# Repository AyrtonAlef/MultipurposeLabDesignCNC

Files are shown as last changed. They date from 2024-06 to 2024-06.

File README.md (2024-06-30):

# Multipurpose Lab-design CNC

Development of a lab-design positioning system (CNC machine) with interchangeable head for different applications.

The positioning system allows precise control of the position and speed of the head along the stage plane. The distance between the head and the stage can be adjusted manually using a hand screw. Three head modules are available: (i) painting head, (ii) pencil head and (iii) cleaning head.

The painting head allows an airbrush to be attached and painting to be carried out in a controlled manner. The module was designed to work with a double-action airbrush. The air flow and paint intensity are controlled by a servo motor.

The pencil head allows a pencil or a pen to be attached. By activating a servo motor, the pencil/pencil is brought closer to the stage, allowing lines or curves to be drawn according to the movement of the positioning system. The pencil head can be used to perform pencil tests. The module ensures that the force, inclination and path traveled are kept constant throughout the test. According to the desired tilt angle, the can be fixed either 45° or 90° in relation to the stage.

The cleaning head includes a linear rod. The rod has a cylindrical end, allowing a cloth to be attached to assess the anti-stain properties of materials. The anti-stain property can be associated with the ease with which the material's surface can be cleaned. Thus, to characterize anti-stain property, the surface being evaluated can be contaminated and then cleaned. Images of the surface are captured before and after cleaning, allowing the surface's susceptibility to cleaning to be quantified. Images of the cloth used for cleaning can also be captured, in order to assess the ability to transfer contaminants to the cloth. To conduct the anti-stain test, it is necessary to ensure reproducibility in both contamination and cleaning steps. By using the cleaning head, it is possible to ensure that the cloth proximity to the contaminated surface, the cleaning path and the force are kept constant throughout the anti-stain test.

The electrical/electronic components, responsible for controlling the positioning system, are contained in a box that functions as a control panel, providing flexibility and safety in the use of the equipment. The control panel can be fully 3D printed, allowing the attachment of control boards (Arduino and CNC shield), command buttons (ON/OFF and emergency button), power source and cooling system.

The control of the positioning system (lab-design CNC) was performed using Grbl. To facilitate the insertion of commands by the user, the Universal G-Code Sender (UGS) was used. Grbl is free, open-source and high-performance software for controlling movement in machines, running directly on Arduino. UGS is a free gcode platform with several features for interfacing advanced CNC controls in different environments, such as Grbl.
In the root folder of the repository there is a text file (InstalationVer2.txt) with several instructions regarding the use of the positioning system. There you will find a description of the main elements used for control (stepper motor and servo motor), links to more information about the control programs used (Grbl, UGS and Arduino) and a step-by-step guide for initializing the device.

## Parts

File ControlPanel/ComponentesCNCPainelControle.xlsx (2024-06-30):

Qtdade | Descrição | Nome
1 | Placa inferior (impresso 3D - PLA) | CaixaBase
2 | Placa lateral (impresso 3D - PLA) | CaixaLateral
1 | Placa traseira (impresso 3D - PLA) | CaixaTraseira
1 | Placa frontal (impresso 3D - PLA) | CaixaFrente
1 | Placa superior (impresso 3D - PLA) | CaixaSuperior
1 | Chave Liga/Desliga | BotaoLigaDesliga
1 | Tomada painel plug conector macho 3 pinos | PlugueAlimentacaoFemea
1 | Arduino UNO R3 | arduino uno
1 | CNC Shield V3 (3D RepRap) | CNC shield.stp
1 | Fonte ATX colméia S60-12 -12 V, 5 A e 60 W Bivolt (Haiz) | Fonte
4 | Driver de motor de passo A4988 | -
1 | Botão de Emergência | BotaoEmergencia
1 | Cooler | Cooler

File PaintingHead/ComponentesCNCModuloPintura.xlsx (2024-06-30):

Qtdade | Descrição | Nome
1 | Suporte aerógrafo (impresso 3D - PLA) | MontagemSuporteAerografo
1 | Suporte traseira superior aerógrafo (impresso 3D - PLA) | SuporteCorpoAerografoVer3Part2
1 | Casco superior corpo aerógrafo (impresso 3D - PLA) | GatilhoSuporteSuperiorVer3
1 | Casco inferior corpo aeerógrafo (impresso 3D - PLA) | GatilhoSuporteinferior
1 | Caminho para acionamento (impresso 3D - PLA) | GatilhoSuporteCaminhoVer2
1 | Corrediça para acionamento (impresso 3D - PLA) | GatilhhoSuporteCorredicaVer2
1 | Capa para o gatilho (impresso 3D - PLA) | GatilhoBotao&HasteBotao_SuporteVer4
1 | Disco furato para servo motor (impresso 3D - PLA) | GatilhoServo
1 | Haste disco-corrediça (impresso 3D - PLA) | GatilhoHasteServo_SuporteVer4
1 | Micro servo motor Tower Pro 9gSg9 (Wtec) | SG90 - MicroServo 9g - Tower Pro.1
1 | Mini compressor de ar ON-10 (Onetools) | -
1 | Aerógrafo dupla ação copo fixo 0,3 mm (Onetools) | Aerografo
1 | Parafuso atarraxante Phillips 2,2x6,5 mm | -
4 | Parafuso Allen M3x25 mm | -
1 | Parafuso Allen M3x8 mm | -
1 | Parafuso Allen M3x10 mm | -
7 | Arruela lisa M3 | -
5 | Porca sextavada M3 | -

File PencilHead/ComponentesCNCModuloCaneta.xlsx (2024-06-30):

Qtdade | Descrição | Nome
1 | Suporte base caneta (impresso 3D - PLA) | MontagemSuporteCaneta
1 | Suporte articulado (impresso 3D - PLA) | SuporteArticulacaoVer2
1 | Suporte caneta 45° (impresso 3D - PLA) | SuporteCaneta90degreesVer2
1 | Suporte caneta 90° (impresso 3D - PLA) | SuporteCanetaVer2
1 | Micro servo motor Tower Pro 9gSg90 (Wtec) | SG90 - Micro Servo 9g - Tower Pro.1
1 | Adaptador conexão com servo motor | SG90 - Micro Servo 9g - Tower Pro.2
2 | Parafuso Phillips M3x30 mm | -
2 | Parafuso Phillips M3x8 mm | -
1 | Parafuso Phillips M2,5x6 mm | -
2 | Arruela lisa M3 | -
2 | Porca sextavada M3 | -
1 | Arruela lisa M2,5 | -
1 | Porca sextavada M2,5 | -

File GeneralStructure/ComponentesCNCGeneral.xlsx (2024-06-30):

Qtdade | Descrição | Nome
1.1 Eixo Y
2 | Chapa 1/2" 420x70 mm (usinado - Al6061) | ChapaBaseDianteiraTraseira
4 | Suporte para guia linear 12 mm | SuporteGuiaLinear12mm
4 | Perfil 20x20 - 420 mm (alumínio) | EixoYPerfil20x20mm
2 | Guia linear 12x420 mm | EixoYHasteLinear12mm
1 | Chapa 1/2" 445,4x300 mm (usinado - Al6061) | Mesa
2 | Rolamento 608zz | Rolamento608xx_8mm
1 | Fuso Tr8 passo 2 mm - 448 mm | EixoYFusoTr8_2mm
4 | Espaçador M3x35 mm | EspaçadorM3_35mm
1 | Acoplamento flexível 5x8 mm | AcoplamentoFlexível5x8mm
1 | Motor Nema 17 - 3,5 kgf.cm e 1,2 A (Action) | MotorNema17_3.5Kgfcm
2 | Micro chave fim de curso KW12 | -
2 | Suporte chave fim de curso (impresso - PLA) | SuporteSwitchFimdeCursoV2
1.2 Eixo X
4 | Pillow block SCS12UU | PillowBlockSCS12UU_12mm
1 | Chapa 1/2" 334x55 mm (usinado - Al6061) | EixoYChapaBase
1 | Bloco Suporte Castanha Tr8 35x28x30 mm (alumínio) | SuporteCastanhaTr8
1 | Castanha Tr8 passo 2 mm | CastanhaTr8_2mm
1 | Chapa 1/2" 270x90 mm (usinado - Al6061) | ChapaColunaDireita
1 | Chapa 1/2" 270x90 mm (usinado - Al6061) | ChapaColunaEsquerda
2 | Perfil 20x20 - 334 mm (alumínio) | EixoXPerfil20x20mm
4 | Suporte para guia linear 12 mm | SuporteGuiaLinear12mm
2 | Guia linear 12x334 mm | EixoXHasteLinear12mm
2 | Rolamento 608zz | Rolamento608xx_8mm
4 | Espaçador M3x35 mm | EspaçadorM3_35mm
1 | Fuso Tr8 passo 2 mm - 360 mm | EixoXFusoTr8_2mm
1 | Acoplamento flexível 5x8 mm | AcoplamentoFlexível5x8mm
1 | Motor Nema 17 - 3,5 kgf.cm e 1,2 A (Action) | MotorNema17_3.5Kgfcm
2 | Micro chave fim de curso KW12 | -
2 | Suporte chave fim de curso (impresso - PLA) | SuporteSwitchFimdeCursoV2
1.2 Eixo Z
2 | Pillow block SCS12UU | PillowBlockSCS12UU_12mm
1 | Bloco Suporte Castanha Tr8 35x28x30 mm (alumínio) | SuporteCastanhaTr8
1 | Castanha Tr8 passo 2 mm | CastanhaTr8_2mm
1 | Chapa 1/2" 160x75 mm (usinado - Al6061) | ChapaBaseEixoZ
1 | Chapa 1/2" 75x30 mm (usinado - Al6061) | ChapaBaseTraseiraEixoZ
1 | Chapa 1/2" 75x30 mm (usinado - Al6061) | ChapaBaseDianteiraEixoZ
2 | Rolamento 608zz | Rolamento608xx_8mm
2 | Guia linear 12x158 mm | EixoZHasteLinear12mm
1 | Fuso Tr8 passo 2 mm - 190 mm | EixoZFusoTr8_2mm
1 | Manípulo M8 | AcionamentoEixoZ
1 | Bloco Suporte Castanha Tr8 35x20x75 mm (usinado - Al6061) | SuporteCastanhaTr8EixoZ
2 | Rolamento linar LM12UU | RolamentoLinearM12UU12mm
1 | Castanha Tr8 passo 2 mm | CastanhaTr8_2mm

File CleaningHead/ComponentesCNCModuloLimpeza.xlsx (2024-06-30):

Qtdade | Descrição | Nome
1 | Suporte haste (impresso 3D - PLA) | Suporte
1 | Haste linear (impresso 3D - PLA) | HasteLinearPontaCirc
1 | Parafuso Allen M6x18 mm | -

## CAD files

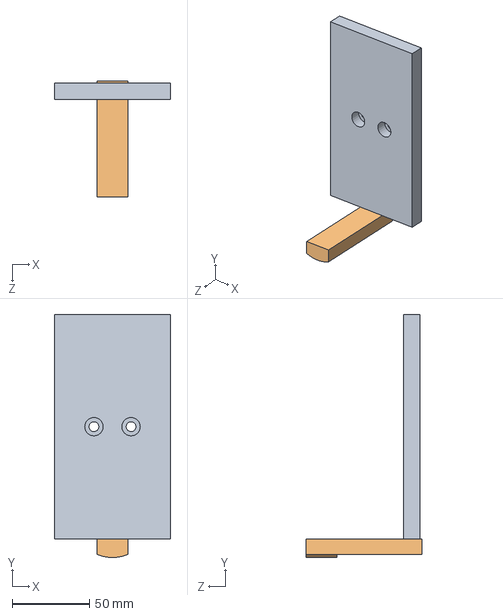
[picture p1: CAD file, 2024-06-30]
CleaningHead/MontagemHaste.SLDASM
75.0 x 157.0 x 75.0 mm
Suporte
HasteLinearPontaCirc

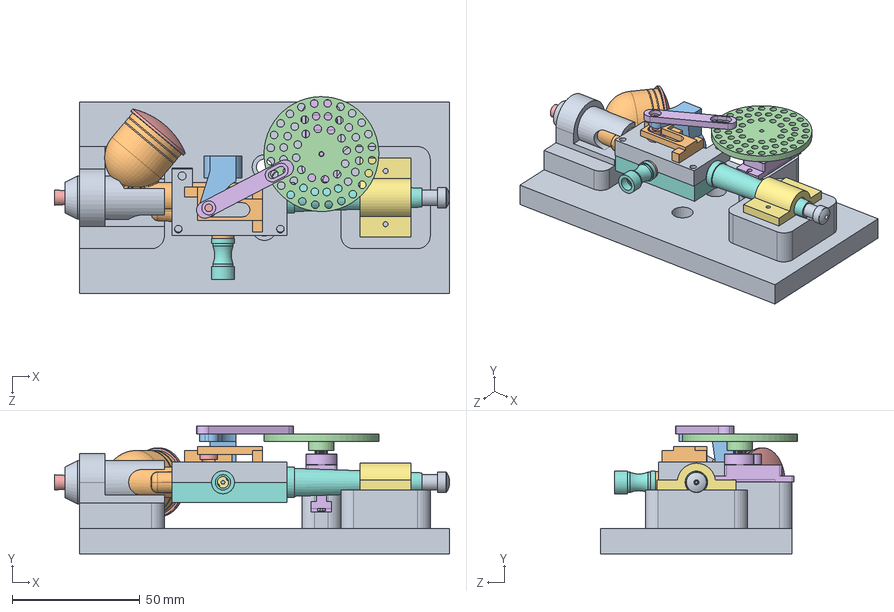
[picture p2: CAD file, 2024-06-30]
PaintingHead/MontagemAerografo.SLDASM
154.7 x 50.0 x 77.0 mm
MontagemSuporteAerografo
Corpo 1
Encaixe_Agulha
Parafuso
Fixação_Agulha_3
Mola_Agulha
Fixação_Agulha_2
Alavanca
Alavanca_Mecanismo
Rebite
Eixo_Valvula
Mola_Valvula
O-ring_Válvula 1
O-ring_Válvula 2
Tampa_Válvula
Valvula
Placa_Mola
O-ring_Bico
O-ring_Corpo
Bico 1
Bico 2
Biqueira
Biqueira 2
Corpo 2
Encaixe_Fundo
Fixação_Agulha
O-Ring_Encaixe_Fundo
Agulha
Tampa
SG90 - Micro Servo 9g - Tower Pro.1
SuporteCorpoAerografoVer3Part2
GatilhoSuporteInferior
GatilhoSuporteSuperiorVer3
GatilhoSuporteCaminhoVer2
GatilhoBotao&HasteBotao_SuporteVer4
GatilhoServo
GatilhoSuporteCorredicaVer2
GatilhoHasteServo_SuporteVer4

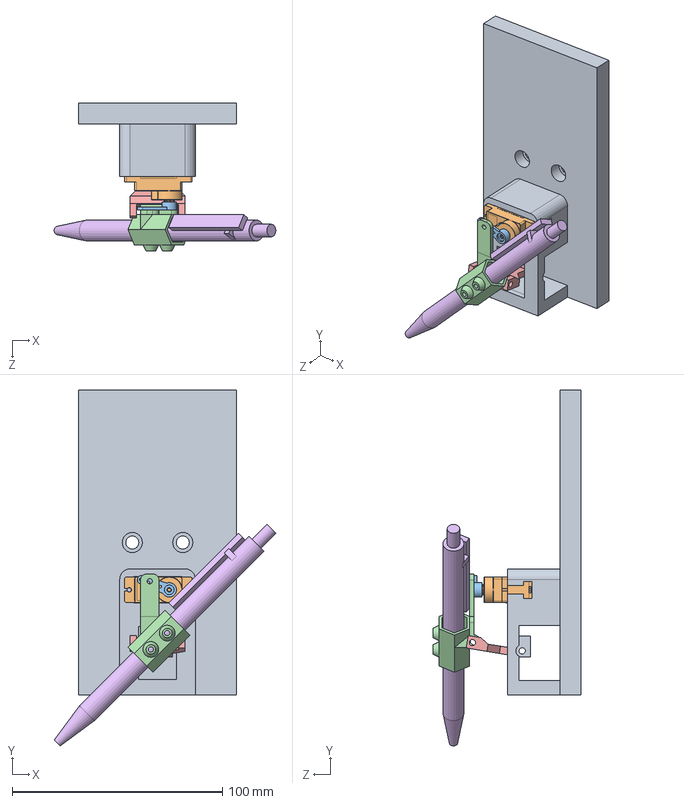
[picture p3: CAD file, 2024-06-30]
PencilHead/MontagemCantea.SLDASM
105.4 x 169.2 x 70.5 mm
MontagemSuporteCaneta
SG90 - Micro Servo 9g - Tower Pro.1
SG90 - Micro Servo 9g - Tower Pro.2
SuporteCaneta90degreesVer2
SuporteArticulacaoVer2
Caneta

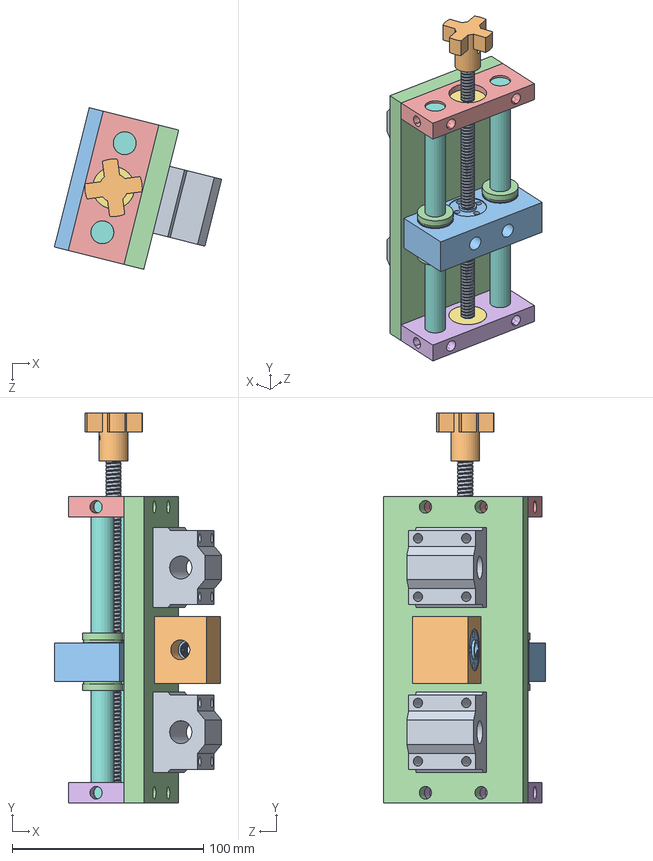
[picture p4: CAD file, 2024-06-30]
GeneralStructure/MaquinaEixoZ.SLDASM
87.4 x 203.7 x 84.5 mm
PillowBlockSCS12UU_12mm x 2
SuporteCastanhaTr8
CastanhaTr8_2mm x 2
ChapaBaseEixoZ
ChapaBaseTraseiraEixoZ
ChapaBaseDianteiraEixoZ
Rolamento608zz_8mm x 2
EixoZHasteLinear12mm x 2
EixoZFusoTr8_2mm
AcionamentoEixoZ
SuporteCastanhaTr8EixoZ
RolamentoLinearLM12UU12mm x 2

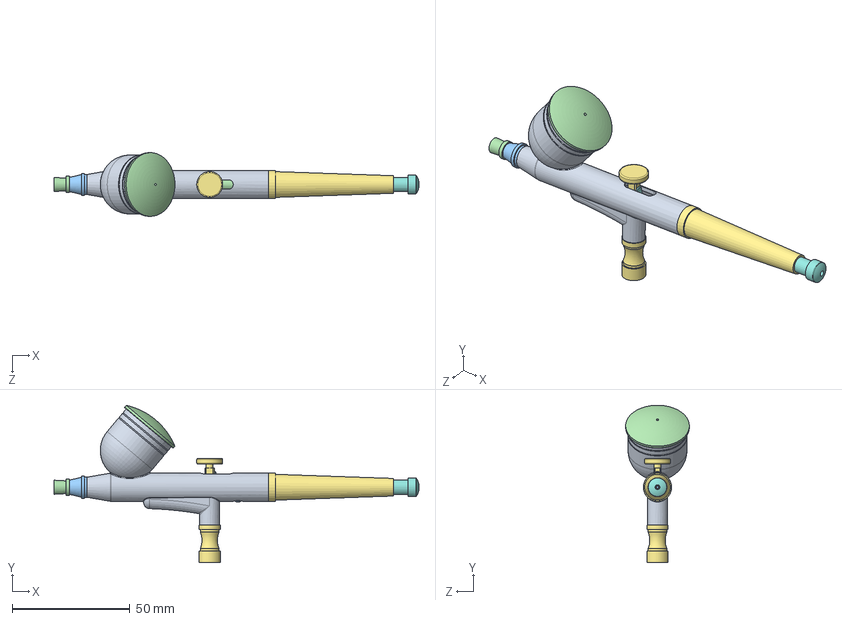
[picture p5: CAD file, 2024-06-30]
PaintingHead/Aerografo.SLDASM
154.7 x 66.7 x 27.0 mm
Corpo 1
Encaixe_Agulha
Parafuso
Fixação_Agulha_3
Mola_Agulha
Fixação_Agulha_2
Alavanca
Alavanca_Mecanismo
Rebite
Eixo_Valvula
Mola_Valvula
O-ring_Válvula 1
O-ring_Válvula 2
Tampa_Válvula
Valvula
Placa_Mola
O-ring_Bico
O-ring_Corpo
Bico 1
Bico 2
Biqueira
Biqueira 2
Corpo 2
Encaixe_Fundo
Fixação_Agulha
O-Ring_Encaixe_Fundo
Agulha
Tampa

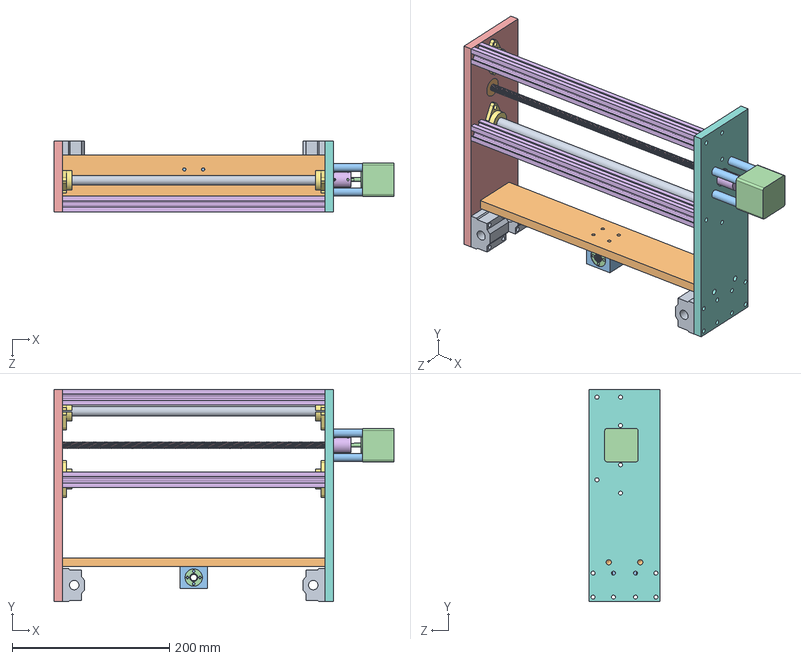
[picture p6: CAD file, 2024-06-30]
GeneralStructure/MaquinaEixoX.SLDASM
432.4 x 270.0 x 90.0 mm
PillowBlockSCS12UU_12mm x 4
EixoYChapaBase
SuporteCastanhaTr8
CastanhaTr8_2mm
ChapaColunaDireita
EixoXPerfil20x20mm x 2
SuporteGuiaLinear12mm x 4
ChapaColunaEsquerda
EixoXHasteLinear12mm x 2
Rolamento608zz_8mm x 2
EspaçadorM3_35mm x 4
MotorNema17_3.5Kgfcm
EixoXFusoTr8_2mm
AcoplamentoFlexível5x8mm

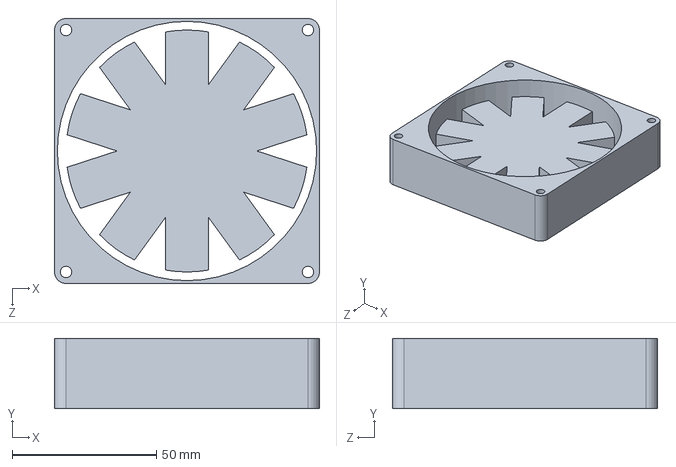
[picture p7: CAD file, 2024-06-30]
ControlPanel/Cooler.SLDPRT
92.0 x 24.4 x 92.0 mm

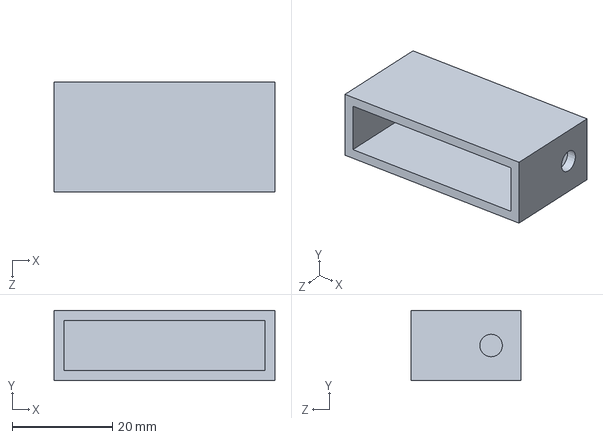
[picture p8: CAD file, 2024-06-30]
GeneralStructure/SuporteSwitchFimdeCursoV2.SLDPRT
44.0 x 14.0 x 22.0 mm

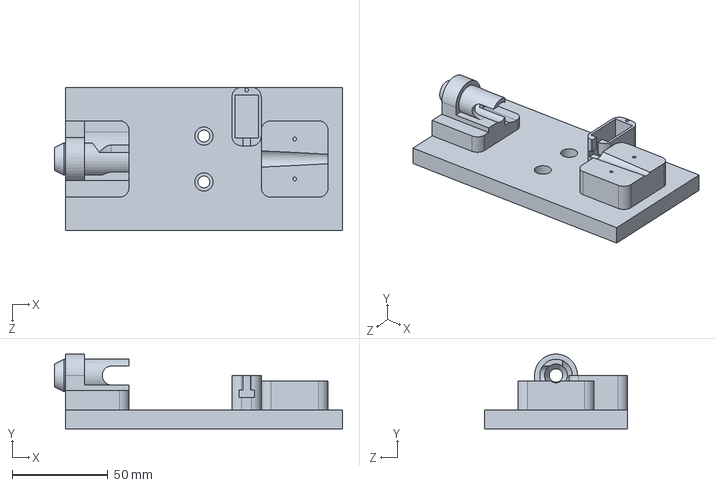
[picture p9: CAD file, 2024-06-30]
PaintingHead/MontagemSuporteAerografo.SLDPRT
150.7 x 39.2 x 75.0 mm

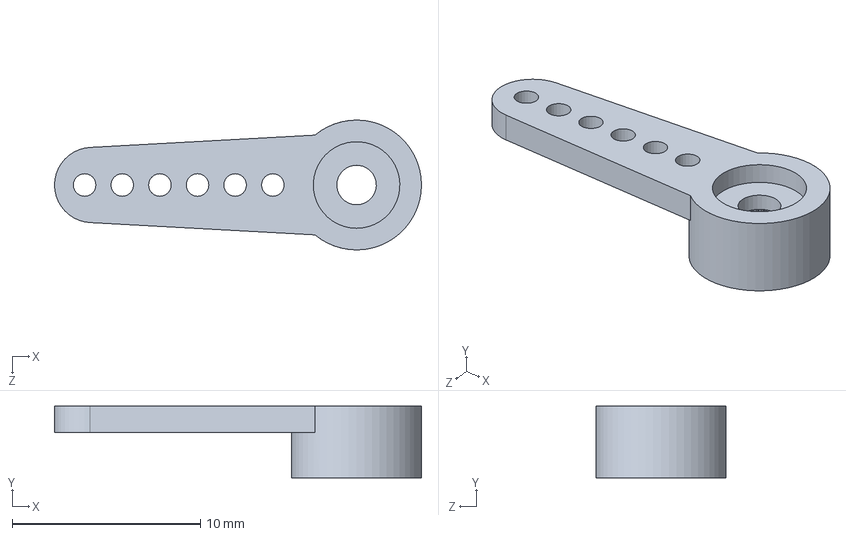
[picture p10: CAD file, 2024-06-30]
PencilHead/SG90 - Micro Servo 9g - Tower Pro.2.SLDPRT
19.5 x 3.80 x 6.90 mm

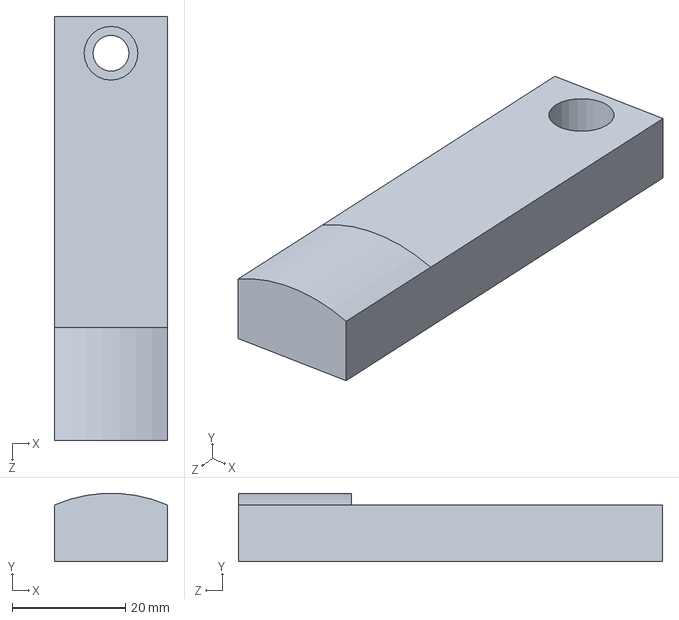
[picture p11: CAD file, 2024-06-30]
CleaningHead/HasteLinearPontaCirc.SLDPRT
20.0 x 12.0 x 75.0 mm

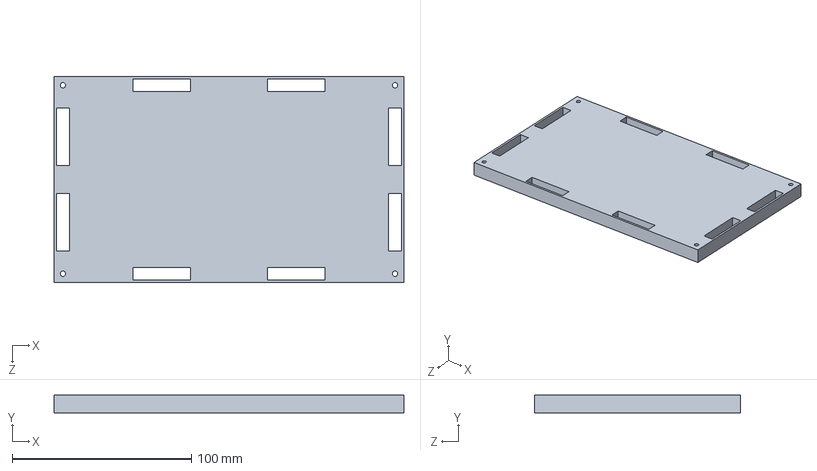
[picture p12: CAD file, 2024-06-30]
ControlPanel/CaixaBase.SLDPRT
195.0 x 10.0 x 115.0 mm

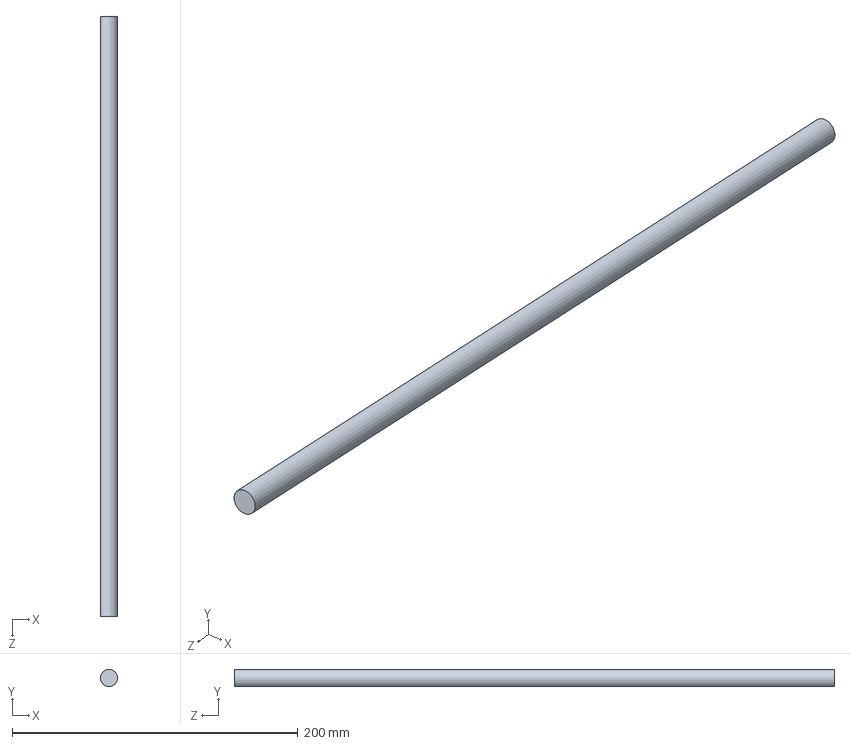
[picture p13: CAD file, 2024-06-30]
GeneralStructure/EixoYHasteLinear12mm.SLDPRT
12.0 x 12.0 x 420.0 mm

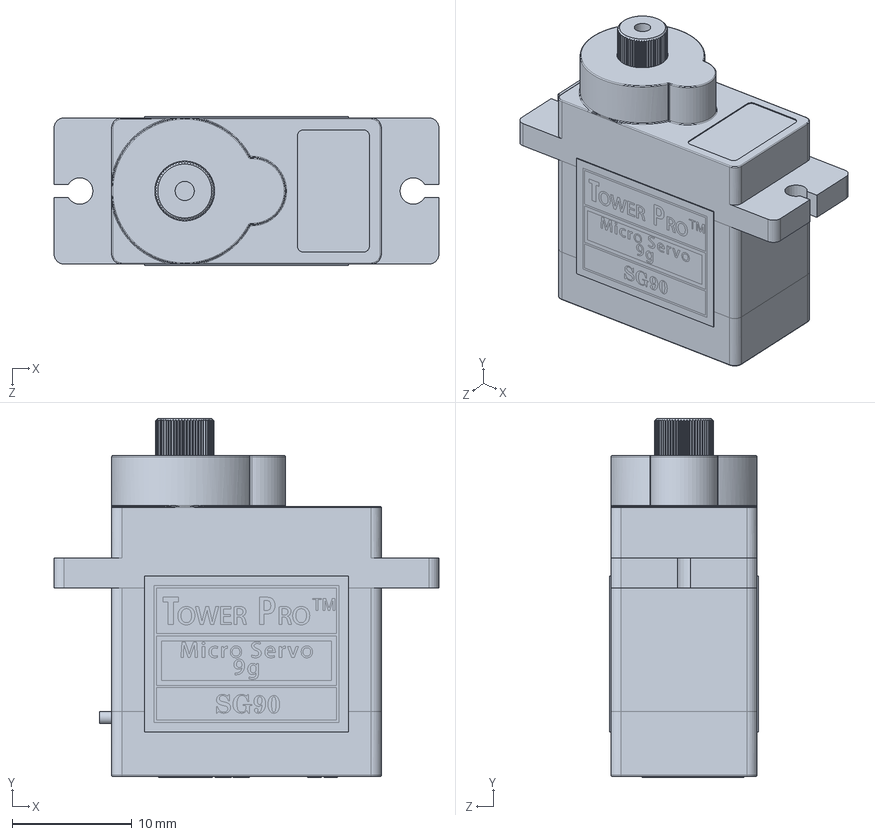
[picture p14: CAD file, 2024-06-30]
PaintingHead/SG90 - Micro Servo 9g - Tower Pro.1.SLDPRT
32.1 x 30.0 x 12.4 mm

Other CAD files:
PencilHead/MontagemSuporteCaneta.SLDPRT
ControlPanel/PlugueAlimentacaoFemea.SLDPRT
GeneralStructure/EixoXPerfil20x20mm.SLDPRT
CleaningHead/HasteLinearPontaCirc.STL
ControlPanel/BotaoEmergencia.SLDPRT
ControlPanel/BotaoLigaDesliga.SLDPRT
ControlPanel/CaixaBase.STL
ControlPanel/CaixaFrente.SLDPRT
ControlPanel/CaixaFrente.STL
ControlPanel/CaixaLateral.SLDPRT
ControlPanel/CaixaLateral.STL
ControlPanel/CaixaSuperior.SLDPRT
ControlPanel/CaixaSuperior.STL
ControlPanel/CaixaTraseira.SLDPRT
ControlPanel/CaixaTraseira.STL
ControlPanel/Fonte.SLDPRT
GeneralStructure/AcionamentoEixoZ.SLDPRT
GeneralStructure/AcoplamentoFlexível5x8mm.SLDPRT
GeneralStructure/CastanhaTr8_2mm.SLDPRT
GeneralStructure/ChapaBaseDianteiraEixoZ.SLDPRT
GeneralStructure/ChapaBaseDianteiraTraseira.SLDPRT
GeneralStructure/ChapaBaseEixoZ.SLDPRT
GeneralStructure/ChapaBaseTraseira.SLDPRT
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

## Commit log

2024-06-30 Upload files general structure
    [AcionamentoEixoZ.SLDPRT, AcoplamentoFlexível5x8mm.SLDPRT, CastanhaTr8_2mm.SLDPRT, ChapaBaseDianteiraEixoZ.SLDPRT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]
2024-06-30 Upload control panel files
    [BotaoEmergencia.SLDPRT, BotaoLigaDesliga.SLDPRT, CaixaBase.SLDPRT, CaixaBase.STL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]
2024-06-30 Upload SuporteFimdeCurso
    [SuporteSwitchFimdeCursoV2.SLDPRT, SuporteSwitchFimdeCursoV2.STL]
2024-06-30 Upload printing head files
    [Aerografo.SLDASM, GatilhoBotao&HasteBotao_SuporteVer4.SLDPRT, GatilhoBotao&HasteBotao_SuporteVer4.STL, GatilhoHasteServo_SuporteVer4.SLDPRT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]
2024-06-30 Upload pencil head files
    [Caneta.SLDPRT, MontagemCantea.SLDASM, MontagemSuporteCaneta.SLDPRT, MontagemSuporteCaneta.STL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]
2024-06-30 Upload cleaning head files
    [HasteLinearPontaCirc.SLDPRT, HasteLinearPontaCirc.STL, MontagemHaste.SLDASM]
2024-06-30 Upload component description
    [ComponentesCNCGeneral.xlsx]
2024-06-30 Upload component pencil head description
    [ComponentesCNCModuloCaneta.xlsx]
2024-06-30 Upload component cleaning head description
    [ComponentesCNCModuloLimpeza.xlsx]
2024-06-30 Upload component painting head description
    [ComponentesCNCModuloPintura.xlsx]
2024-06-30 Upload component control panel description
    [ComponentesCNCPainelControle.xlsx]
